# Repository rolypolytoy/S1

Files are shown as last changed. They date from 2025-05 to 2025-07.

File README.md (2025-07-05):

# S1 Desktop SEM

S1 is an open-source, low-cost, high-performance scanning electron microscope (SEM) project, which doubles as a reasonably accurate e-beam lithography machine, because why not?

| Metric            | Estimated     | Achieved | Method                  |
| ----------------- | ---------- | -------- | ----------------------- |
| Ultimate Resolution    |<<100nm     | TBD      | Reconstructing the Paper |
| Vacuum Pressure   | <10⁻⁵ Torr | TBD      | HV Diffusion Pump, Embedded Pressure Gauge.|

---

## System Overview

### Vacuum Integrity
View

[Roughing pumps](https://www.amazon.com/Orion-Motor-Tech-Conditioner-Servicing/dp/B08P1W6Z8D) can be bought quite cheaply on amazon for about $70, and can pump down to the 1e-2 torr order of magnitude, which is good enough as a backing pump for most high-vacuum pumps. This one is 37.5 microns, which converts to around 3e-2 torr, which is good enough for diffusion pumps.

Most pumps of this kind have an around 1/4th inch diameter outlet, and so you can buy 1/4th inch ID [vinyl tubing](https://www.amazon.com/Flexible-Lightweight-Plastic-Chemical-Resistant/dp/B09Y5R8SSL). 

Finally- FCStd files for the Diffusion Pump are uploaded [here](https://github.com/rolypolytoy/S1/blob/main/Vacuum%20Integrity) and at the [Diffusion Pump](https://github.com/rolypolytoy/diffusion_pump) project. It's already built to be integrated with 1/4th inch vinyl pipes, so simply slip the pipe around the machined diffusion pump. We also use KF25 flanges and conventional water cooling with a pump, to ensure it stays cold.

For the O-ring, buy 130 mm ID, 2 mm thickness [Nitrile O-rings](https://www.amazon.com/uxcell-Rings-Nitrile-125-2mm-Diameter/dp/B07HGCCHNZ) to seal the flange between the diffusion pump and the connector to the vacuum pump.

The holes on the side of the flanges are around 6.4 mm in diameter, so use 8 M6 to tighten, once the O-ring is inside the groove, and the connector has been welded to the frame. 

We'll use the [KJL 704](https://www.agarscientific.com/vacuum-diffusion-pump-fluids) diffusion pump oil for 125.77 pounds from agar scientific, which has an untrapped ultimate vacuum of 1e-7 to 1e-8 torr and trapped of 1e-11 torr. Kurt J Lesker also sells 500 ccs directly for [120 dollars](https://www.lesker.com/newweb/fluids/diffpumpoils-silicone-kjlc/), and so this is really good cost-price.

The nichrome wire I'm using can heat up to 800W so we're good in terms of heating since resistive heating implements are the only implements with 100% efficiency, and 800W is more than enough to heat a diffusion pump of this size and we're using a [server fan](https://www.amazon.in/Delta-Electronics-AFB1212GHE-CF00-120x120x-connector/dp/B004X2M2GG) with 241 CFM- it's noisy but it's better than a water cooling system I know that, so about 200W of dissipation might be viable.

We'll use dovetail sliding doors, nitrile tubing, and screw clamps for the sliding door.

### Embedded Systems

All power sources are kept outside and funneled in- this is because power supplies have electrolytic capacitors that will 100% burst in a vacuum. All our embedded stuff is designed to have none of this.

The power supply comes from mains through a plug, and we have a [10kVDC](https://ar.aliexpress.com/item/1005003518403820.html) power source, as well as a [60VDC](https://www.amazon.in/Adjustable-05-60Volt-Variable-Converter-600Watts/dp/B0F3KJ5VNP) power source that connects w/mains.

- **Microcontroller**:  
  - [Teensy 4.1](https://www.amazon.in/4-1-iMXRT1062-Development-soldered-Pre-soldered/dp/B0DP6M197Q) (no electrolytic capacitors, which make it safe for vacuum pressures due to no outgassing or capacitor ruptures)
  - Works with the Arduino framework with [Teensyduino](https://www.pjrc.com/teensy/td_download.html).

- **Electron Detector**:  
  - [Plastic scintillator with 425 nm emission](https://www.alibaba.com/product-detail/Polystyrene-Plastic-scintillator-material-equivalent-EJ_1601298622046.html?spm=a2700.7724857.0.0.6c196c9eovIgdM). It's a 10mmx10mmx1mm cuboid.
  - [Onsemi SiPM with 420 nm peak sensitivity](https://www.mouser.in/ProductDetail/onsemi/MICROFC-30035-SMT-TR?qs=byeeYqUIh0Mh9KJVNOFZEA%3D%3D). I've taken the CAD file for this and put it in the CAD folder. Its rise time is 0.6nS, and at 420nM it has over 40% of particles detected. It has a 300 ps pulse with a 600 ps pulse width. It has several white papers on its characteristics. In [this one](https://www.onsemi.com/pub/collateral/and9770-d.pdf) we can see its breakdown voltage is ~24.6 V and in [this one](https://www.onsemi.com/download/white-papers/pdf/tnd6262-d.pdf) we can see its recommended overvoltage is 5.0V so 30VDC is a very, very good voltage and we can make it with the 60V power supply with a basic voltage divider. They have either a fast pulse or a normal pulse mode, we'll use normal pulse mode. 
  - [Cremat CR-110](https://www.amazon.ae/CR-113-R2-1-Charge-Sensitive-preamplifier-Module/dp/B07BCQSBD8) charge-sensitive preamplifier (µs-long pulses, 7 ns rise time) to read current from the silicon photomultiplier, and it needs a +-10V (12V total) power supply. The pulses from this are 7ns in terms of rise time and decay slower. 
  - [Cremat CR-200-500ns](https://www.amazon.ae/Cremat-Inc-CR-200-500ns-R2-1-Shaping-Amplifier/dp/B07BD28Y7R?) pulse shaper (500 ns pulses) so the ADC can read from it. Needs the same power as the CR-110. Shapes it into Gaussian pulses and amplifies it a bit more post-CSA so this should be in the hundreds of mV/low V range, but regardless will be within the ADC's 16 bits of range.
  - The [AD7626BCPZ](https://www.mouser.in/ProductDetail/Analog-Devices/AD7626BCPZ-RL7?qs=%2FtpEQrCGXCwjx1S0Wpoj8A%3D%3D)- a 10 MSPS ADC (exceeds the 2 MSPS requirement for 500 ns pulses, with roughly 5 samples/pulse- good for SNR). So, we can quite easily sample at 2MHz with this signal processing pipeline which is good enough for electron microscopy. Uses LVDS so we'll definitely need a chip for it which is [this one](https://www.mouser.in/ProductDetail/Texas-Instruments/DS90CR286ATDGGRQ1?qs=8%2FmU9qzJpL9GnwtExKjdYg%3D%3D). So we have a functional design for an electron detection pipeline at fast enough speeds for our needs.

I'll obviously use a blue LED on the photomultiplier-cremat-ADC setup to see if it works before assembling the ET detector.

Some auxiliary setup information not in the CAD: 
The first two condenser lenses must have 920 turns and the objective lens 600 turns in a solenoidal arrangement inside the housing. 

The EE bit is done, all that remains is the embedded system code & companion app (Teensyduino and QT via PySide6, Pyintaller, PyUSB, PySERIAL on pypi respectively).

### CAD
I found an [old paper](https://github.com/rolypolytoy/S1/blob/main/SEM_Design.pdf) which outlines how to design a 10-nm resolution SEM with exact current, current densities (so of course we can reconstruct the gauge they used, which I did, and it's 14 AWG), condenser 1, 2, and objective lens specs, beam column design, full ray tracing with commercial FEM, and so the design work has been done already. Of course this means all the work we did in the electron column is useless but honestly basically guaranteeing nm-scale resolution is worthwhile. Even if we don't get 10 nm resolution, it's going to get sub-micron resolution. The condenser lens 1 is centered at 80mm below the Wehnelt cap aperture (at 100.45mm). The second condenser lens is centered at 165mm below, or at -64mm-ish. Final focus is at 301mm, and the assembly of the objective lens must end at 290mm. This is all, as per the latest CAD file, is entirely valid and so the dimensions are all entirely correct. 

Additionally I've finished the CAD for the electron column including the Wehnelt cylinder, anodes, and lenses. There wasn't information on the pole piece bore size in the SEM paper so I found a patent for a magnetic lens design and it showed that the normal range was from 1 mm to 3 mm, so I've taken a 4 mm bore diameter for the condenser lenses and 1 mm for the objective lens (US5563415A if you're looking for it, but I have the pdf in the repo regardless). It expired in 2015- [proof here](https://patents.google.com/patent/US5563415A/en?oq=5%2c563%2c415), so we're entirely able to use it. In general there are a lot of US patents on electromagnetic lenses [here](https://patents.google.com/?q=H01J37%2f141).

Another expired patent I found really useful is a full design of an SEM that expired in 1992: [US3924126A](https://patents.google.com/patent/US3924126A/en?q=H01J37%2f141). It's not as useful as the paper because it doesn't include full dimensions, but it's a sanity check and it has some useful information about alignment, some dimensions that weren't mentioned in the paper, and aperture-related info. So, another good source.

For the pole piece: one internal piece, one external piece, attached w/screws. 3A current, 2.8A current, 1.1 A current. 14 AWG wire. Center of condenser lens at 80mm, Focal position 1 at approx. 100mm, Center of Condenser 2 at 164mm, Focal position 2 at approximately 170 mm, center of Objective at 295mm and focal position at 315 mm. 1000 micrometer beam-limiting aperture at 80mm, 100 micrometer beam-limiting aperture at 200mm. Luckily all the apertures are 'inside' the lenses so we don't have to worry about them when constructing the structural parts.

A 500 micrometer aperture as the condenser aperture at 60 mm and a 200 micrometer aperture as the objective aperture at 280 mm.

We also need ~500m of 14 AWG aluminium wire which is either insulated or enameled, for as cheap as possible, which is roughly 14.5 USD, and definitely under 100

Every exterior of the EM lens should be in 4 pieces, and the pole piece as 1. Design the CAD files of these next. Scanning coils (solenoid), stigmators (octupole), and alignment coils (quadrupole) also necessary using 14AWG Al wire where relevant.

For the yoke of the magnetic lenses we'll use electrical steel, and for the pole piece we'll use 99.95% iron (electropolished and nickelplated ofc).

Make a singular CAD Assembly file with all details.

I've fully reconstructed the specs from the paper. Here's an exploded view of all the non-structural components- you can see the housing, pole pieces, Wehnelt caps etc etc:



Non-exploded view of the frame with diffusion pump attached:



View of all the analog & power electronics via a circuit schematic: 

Circuit

This is in the repo as Column.FCStd, of course. All the sizes are exactly as taken down to the mm from the paper, and I've made structural components for everything as well. The baseline weight of the frame is ~32 kg and if made of Al 6061 should cost on the order of $100, and the full frame w/sliding doors (metal to metal seal w/ambient air pressure pushing on it) is in Frame.FCStd.
      
  - **Cable feedthroughs**:
    -   Our current approach to making flanges is to, when the frame is being machined, make precise holes in the exterior, pass silicone wires through, and use vacuum-tolerant epoxy. This is expensive, but believe it or not, significantly less expensive than buying feedthroughs for 230VAC, 24VDC, USB, etc, etc. We use [Loctite Stycast-2850](https://in.rsdelivers.com/product/loctite/loctite-stycast-2850-ft-quartkit/loctite-loctite-stycast-2850-ft-quartkit-black-1/2349630)- a state of the art vacuum epoxy, which means this "makeshift" setup is actually more than satisfactory for HV, and really only gets iffy when you get down to UHV. Additionally- silicone doesn't outgas a lot, so using silicone-insulated wires isn't a no-no, but even if it is, taping over it with PTFE tape is an extremely easy (and cheap) workaround which doesn't compromise anything, or introduce any irregularities into the system.
  
  - **Stage platform**:
    - We use a cheap but micron-level accuracy open-loop stage by buying 3 instances of these [1-axis CNC stepper motor setups with 50 mm stroke length](https://ar.aliexpress.com/item/1005007308081154.html), combining it with three instances of the legendary [TM2209 motor driver](https://www.amazon.in/TESSERACT-TMC2209-V2-0-Ultra-Silent-Motherboard/dp/B08QPLL28G) which has 1/256 microstepping, which means we get micron-level resolution in XYZ. This is particularly important for beam clarity because this means we can use autofocus and vary the z-axis, instead of needing to vary the voltage to the objective lens, which makes our power electronics considerably simpler because we can just use static voltage dividers for all our high-voltage components and implement autofocus by modifying the z-axis and checking if the image is in-focus or out of focus. 

In-House Manufacturing for Al 6061 parts (via manual milling and lathes, for critical vacuum chamber bits sanding with 220 to 3000-grit), Polypropylene (via manual milling and lathing with up to 2000 grit), Soft Iron Yokes (via manual milling and lathing, surface finishing with 220 to 2000 grit), Pole Pieces from 99.95% iron (manual milling/lathing, then electropolishing then nickel plating). Before and after assembly clean everything with isopropyl then acetone, in a cleanroom-esque environment with nitrile gloves and basic PPE.

29/5/2025: I've begun looking for the 500 meters of 14/16 AWG Aluminium wire and the CAD components. Stuff's coming together. I'll keep updating this when there's more progress on this end. From what I can tell, getting electropolishing and nickel plating isn't going to be particularly challenging and since our tolerances are more surface finishes than actual manufacturing tolerances it's going to be easy enough to do 'in house'.

30/5/2025: Ordered every non-structural component, will see how things begin to come together. Ultimately, went easier than I expected. Thanks Agar Scientific, Mouser, Amazon, and AliExpress. Still need to find a supplier for 3N-4N soft iron and 500 meters of aluminum wire. I talked to a guy who sells the latter and he laughed me out for such a 'small quantity' asking me to get at least 50 kg (read: 10 km of wire) or not waste his time. You win some, you lose some. I'll provide updates as everything comes in.

31/5/2025: Teensy 4.1's already arrived, as have a few other miscellaneous things. It's fortuitous it arrived so quickly because it means I can troubleshoot my setup and understand the flow of this MCU well. I already have an Arduino kit, I'll solder headers onto it and in general prepare for the full setup prematurely.

12/6/2025: Several things have arrived. All the 3D printed parts are fabricated to within tolerances. The 10kV HV sources have also arrived, as have the ADC, DAC, SiPM, and Cremat signals processing modules. Still no electrical steel, but we've found a supplier for 500 meters of copper wire and ~200 meters have already arrived, with 300 more to go. Soft iron's also found (4N, from AliExpress once more). Progress is progressing.

19/6/2025: We're using soft iron ingots and melting and casting them, so the final supplier issue (on the materials side) is done, and we're officially to assembly. Like a hydra though, there's another issue- the Cremat CR-113 hasn't shipped and they've refunded it, and only the CR-200-500ns has shipped. So we're going to have to make a CSA with an op-amp in a differentiator setup in an SIP package. Doable with KiCAD, and it'll honestly be lower cost and higher perf, so I'm glad it happened. Maybe I'll remake the CSA + pulse shaper in one package, or make a full MCU + signals processing PCB instead of the whole Teensy, DAC, ADC, SiPM, signals processing as modules thing. For a prototype a difficult setup is fine but for production, definitely not. In more good news though- DRDO's [SSPL](https://www.drdo.gov.in/drdo/labs-and-establishments/solid-state-physics-laboratory-sspl), a SOTA government research laboratory in materials science, and Miranda House from Delhi University, are tentatively going to be beta-testers for it when the prototype is assembled, so there's already some steady footing in that direction.

5/7/2025: Bled over into early Q3 2025, which is unfortunate. But the frame is made! Onto machining the internals and assembling the embedded systems stuff. Looks really good so far. Fixed the Cremat CR-113 issue- made a bespoke CSA with 750x higher gain (better for low-current filaments) and half the cost of the 113. I call it [Lightning In A Bottle](https://github.com/rolypolytoy/lightning-in-a-bottle) because it's really good (the op-amp I used is the best on the market), cheaper than the CR-113 by >50%, and bottling charge is basically exactly what a charge integrator is. It's a better name than Cremat anyways. It's already ordered and should arrive in under 2 weeks from PCBPower, they've got all the parts on hand so no waiting around. I also learnt analog design as a side quest so it's probably good that Cremat refunded me.

---

## Development Timeline

| Milestone                            | Target Date |
|-------------------------------------|-------------|
| Full design complete   | ✅ Q1 2025   |
| **Release-ready version (BEHIND TARGET!!!! WE NEED TO GRIND!!!!!!!!)**           | 🟡 **Q2 2025** |
---

---
## Assembly Instructions

I'll update this with photos and instructions the further I get along in the process.

SEM frame:
SEM

3D printed parts:



- Machine it and get it functioning
- Get e-beam lithography tested and functional to <25 nm resolution.

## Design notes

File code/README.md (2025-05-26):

#Embedded/Electric

Power: 60V

TMC2209 (3 motors NEMA11) settings:
Driver 1: MS1=GND, MS2=GND (address 0b00)
Driver 2: MS1=VDD, MS2=GND (address 0b01)
Driver 3: MS1=GND, MS2=VDD (address 0b10)

50 mm stroke 1 mm pitch

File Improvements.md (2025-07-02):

Monolithic PCB for analog and digital processing- plugs in, plugs out etc.

Monolithic PCB for power electronics- main inputs, coax cable outputs for different powers.

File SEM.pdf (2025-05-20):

Journal of Mechanical Science and Technology 22 (2008) 1734~1746

www.springerlink.com/content/1738-494x DOI 10.1007/s12206-008-0317-9

Journal of

### Mechanical Science and Technology

## Design and fabrication of a scanning electron microscope using a finite element analysis for electron optical system

### Man-Jin Park¹

### , Dong Hwan Kim²

### , Keun Park²

,

### Dong Young Jang³

### and Dong-Chul Han⁴,*

1
School of Mechanical and Aerospace Engineering, Seoul National University, Shinlim-Dong San 56-1, Seoul 151-742, Korea 2 School of Mechanical Design and Automation Engineering, Seoul National University of Technology,
172 Gongreung-dong, Nowon-gu, Seoul 139-743, Korea 3
Department of Industrial Information and System Engineering, Seoul National University of Technology,
172 Gongreung-dong, Nowon-gu, Seoul 139-743, Korea 4
School of Mechanical and Aerospace Engineering, Seoul National University, Shinlim-Dong San 56-1, Seoul 151-742, Korea

(Manuscript Received December 28, 2007; Revised March 24, 2008; Accepted March 26, 2008)

--------------------------------------------------------------------------------------------------------------------------------------------------------------------------------------------------------------------------------------------------------Abstract

In this paper, we describe the design and fabrication of a thermionic scanning electron microscope (SEM) and examine its characteristics analytically. In the design process, the dimensions and capacity of the SEM components, such as the electron column, lenses, and apertures, were determined using finite element analysis. All components were integrated systematically during fabrication in order to achieve the maximum performance by adjusting the lens parameters, high voltage source, and image calibration methods. As a result, a thermionic SEM image with high resolution was achieved. We discuss the primary considerations required to achieve a high-performance image.

Keywords: Scanning electron microscope; Thermal emission; Electromagnetic lens; Finite element analysis --------------------------------------------------------------------------------------------------------------------------------------------------------------------------------------------------------------------------------------------------------

### 1. Introduction

With recent advances in nanotechnology, various
pieces of measurement and analysis equipment have become indispensable for measuring nanoscale objects. Successful research in nanotechnology depends on high-performance measurement or analysis equipment; therefore, the development of such equipment is of great importance. In particular, the scanning electron microscope (SEM) is an important tool used to observe surfaces and analyze nanoscale material components.
The history of electron microscopy began with the development of electron optics [1]. In 1926, Busch studied the trajectories of charged particles in axially symmetric electric and magnetic fields, and laid the foundation for geometrical electron optics when he showed that such fields could act as particle lenses. Nearly at the same time, the French physicist de Broglie introduced the concept of electron waves. A frequency and hence a wavelength was associated with charged particles: this marked the beginning of wave-electron optics. Following these two discoveries in electron optics, the idea of an electron microscope began to take shape [1].
SEMs can be classified into two groups: thermionic and field emission. A field emission SEM has the highest magnification capability and is widely used in industries and research [2-4]. However, field emission SEMs are extremely expensive and require a high level of precautions, including an ultra high vacuum and a clean room, compared to thermionic SEMs. The need for SEMs in the semiconductor industry continues to increase. However, the measurements are a slow process as the SEM scans the object using an

*
Corresponding author. Tel.: +82 2 880 7139, Fax.: +82 2 883 1513 E-mail address: dchan@amed.snu.ac.kr
© KSME & Springer 2008

M.-J. Park et al. / Journal of Mechanical Science and Technology 22 (2008) 1734~1746 | 1735

electron beam. To eliminate this drawback, a miniature and potentially portable SEM with small column dimensions or a multiple column arrangement has been developed [5, 6], but it suffers from poor resolution.
SEMs use extremely short wavelengths (smaller than the wavelength of visible light) to enhance the resolution. Compared to an optical microscope that uses a visible light source with a wavelength of 300 to 700 nm, SEMs use an electron source with a wavelength of 1 nm. The structure and principle of SEMs are similar to optical microscopes. Optical lenses for focusing light in optical microscopes are substituted by electromagnetic lenses for focusing electron beams in SEMs. The electromagnetic lenses cause the electron beam to focus or diverge, depending on the electric current applied on the coils.
In this article, we describe the design and fabrication of a thermionic compact SEM with better performance in terms of resolution and image stability. Our high-resolution SEM is user-controlled and operates using a monitor. Before designing our SEM, beam trajectory analyses in the SEM column were performed for various types of lenses and apertures using the OPERA-3D [7] software. These analyses provided guidelines that resulted in an efficient SEM. Optimal design aspects for various parameters, such as the number of apertures and their arrangement, the pole-piece design of the magnetic lenses, and the excitation current conditions for the magnetic lenses, were considered. We used the simulations to investigate the effect of these design parameters on the SEM performance.

### 2. System fabrication and experiments

A thermionic SEM consists of various mechanical and electrical parts, including an electron gun, a column, a stage, a chamber, electromagnetic lenses, and a controller generating an appropriate current in each coil. Fig. 1 shows a three-dimensional (3D) drawing of a thermal SEM. Fig. 2 illustrates all the components in the electron optical column of our developed SEM; each component was designed and placed to maximize the focusing capability and to enhance the resolution. It is evident from Fig. 2 that the SEM is not very large: the dimensions of the column and the chamber together are only 510 × 460 × 500 mm. The following sections describe the development of the key components of our thermionic SEM.

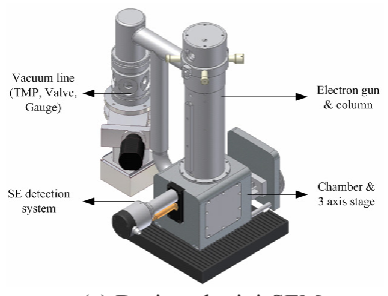
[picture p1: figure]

(a) Designed mini-SEM | (b) Case surrounding the mini-SEM

Fig. 1. 3D image of our fabricated thermal SEM:

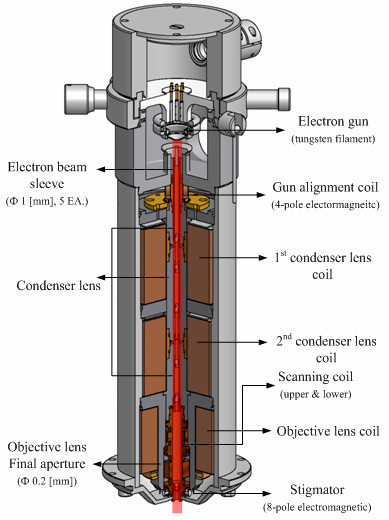
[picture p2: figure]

(a) Section view

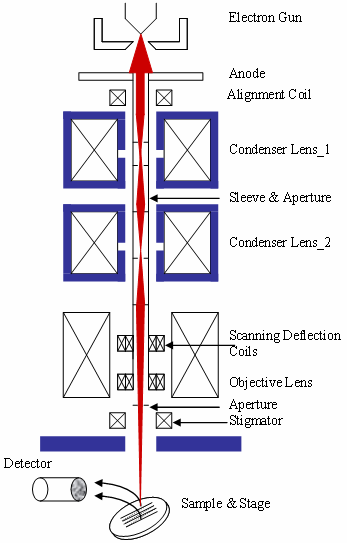
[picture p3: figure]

(b) Schematic diagram of the lens

Fig. 2. Assembled electron optical components (electron gun and electron optical column): (a) section view and (b) schematic diagram of the lenses.

1736 | M.-J. Park et al. / Journal of Mechanical Science and Technology 22 (2008) 1734~1746

### 2.1 Electron beam emission characteristics of ther-

mal electron gun

The electron gun consisted of three electrodes: the cathode, Wehnelt cylinder, and anode. The cathode consisted of a tungsten wire filament bent in the shape of a hairpin with a diameter of 0.15 mm. It decreased the electron beam diameter to guarantee minimal electron emissions at the filament end point. This filament operated stably at 2700 K. The cathode had a low work function (4.5 eV) and high mechanical strength to ensure long-term operation. Tungsten cathodes are widely used because they are both reliable and inexpensive. The Wehnelt cylinder induced the electron beam production from the cathode. It was fabricated and tested many times to ensure the reliability and stability of the electron beam source. The

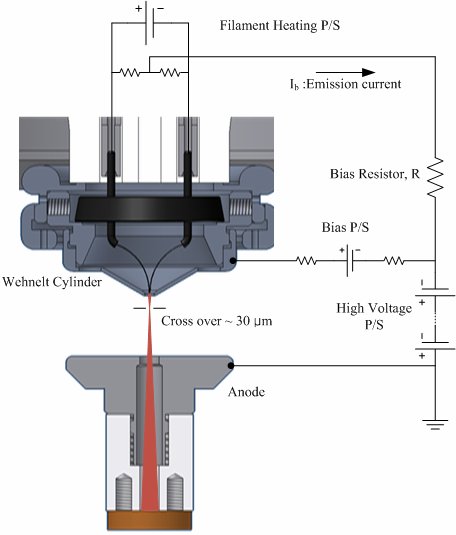
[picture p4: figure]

Fig. 3. Configuration of a thermionic emission gun.

anode was used to accelerate the electron beam after it left the cathode, induced by the Wehnelt cylinder. In addition to a high-voltage source, the electrical power system consisted of three parts that helped with the emission of electrons by controlling the heating of the filament, induction of the cathode, and acceleration of the electron beam. When scanning the electron beam, the high voltages applied on the electrodes should be stable without severe voltage ripples. Our fabricated high-power source had ripples that were less than 10⁻³ % of the reference voltage. The voltages applied on the tungsten filament, cathode, and Wehnelt cylinder ranged from -5 to 25 kV, and the anode was electrically grounded. The electrons emitted from the filament produced a crossover at the Wehnelt, which was under a negative biased voltage in the range of 3 kV, as shown in Fig. 3. The electrons were subjected to a strong acceleration towards the anode due to this high voltage difference between the cathode and the anode. The accelerated electrons reached the specimen through subsequent focusing lenses built in the electron optical column.
A half-fixed biased gun was employed to maintain a high stability and beam current in the gun structure. Thermal emission experiments were performed in a specially manufactured vacuum chamber; the vacuum level inside the chamber was maintained under 10⁻⁵ torr. The emitted electron beam went into a narrow sleeve that functioned as a wave guide and was made of a conductive phosphorous copper. The emitted electron beam current, which passed through a 5 mm hole, was measured at a Faraday cup connected to an electrometer (Keithley 6517) that could measure picoampere-level current. The electron beam was

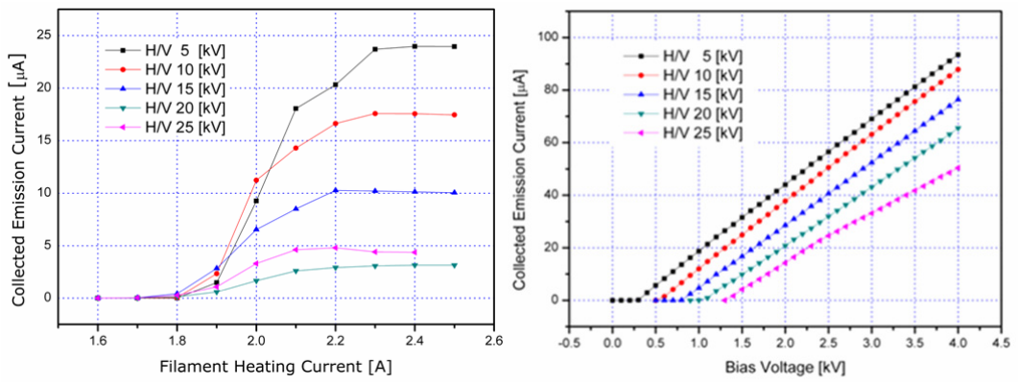
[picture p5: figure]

(a) Filament heating current | (b) Bias voltage

Fig. 4. Variation in the electron emission current with the filament heating current and bias voltage.

M.-J. Park et al. / Journal of Mechanical Science and Technology 22 (2008) 1734~1746 | 1737

aligned mechanically and electrically in the electron gun to measure the electron beam current at the Faraday cup. The beam emission currents were measured as shown in Fig. 4(a) by increasing the filament current from 1.6 through 2.6 A in steps of 0.1 A for five applied acceleration voltages (5, 10, 15, 20 and 25 kV). Around 2.3 A, the current reached a saturation point for all applied voltages. For each acceleration voltage, the changes in the emission current were also measured by changing the bias voltage; these results are illustrated in Fig. 4(b).
The emission current increased as a high bias voltage was imposed on the Wehnelt. Since the emission current and the bias voltage have a linear relationship, an appropriate bias voltage selection is recommended for a large electron beam.
The bias between the cathode and the Wehnelt is often produced by a simple feedback consisting of a resistor connected in series with the cathode. As the electron current emitted from the cathode increases, the cathode becomes more positive with respect to the Wehnelt so that the emitted current is stabilized. The preferred arrangement is to use an electric stabilizer circuit that monitors the beam current and alters the bias voltage to keep the current constant. The purpose of the Wehnelt electrode is to control the electric field close to the cathode so that electrons are emitted from only a small area of the cathode and are subsequently focused into a narrow beam suitable for further demagnification by a series of electron lenses to form the final electron probe. Normally such guns are designed and adjusted so that the electron beam is forced into a narrow “crossover spot” at a short distance beyond the anode, which is then demagnified to form the final probe.

### 2.2 Electromagnetic lenses

The lenses in a SEM play a vital role in demagnifying the electron beam to obtain a focused beam spot. A magnetic lens is most frequently used for narrowing the beam by driving a magnetic field-applied electric current on the coil[8]. By changing the coil current, the focal length can be adjusted, ensuring a highly focused beam. This magnetic flux causes the electron beam to deflect, which is explained by Lorenz’s law. We used two condenser lenses and one objective lens to demagnify the electron beam spot size down to a few nanometers from the large crossover diameter at the Wehnelt cylinder in the electron gun. The condenser lenses, objective lens, and lens apertures were installed serially along the beam trajectory axis, yielding a successively more focused electron beam. The condenser lens, located right after the anode, functioned as a first focusing device for the electron beam, while the second condenser lens also focused the electron beam to demagnify it again. The smaller the beam spot size achieved by the combination of the condenser lenses, the higher the resolution. Once past the condenser lenses, the electron beam was further focused by the objective lens before finally striking the specimen. The aperture was a small hole made of a non-magnetic refractory metal. It intercepted the electrons that passed through the periphery of the lenses and allowed only electrons in the dominant part of the whole electron beam to pass through. Several apertures were placed in the center of the electron beam. The size of the last aperture was predominant in determining the beam size, brightness, diverging angle, and depth of focus. The smaller the last aperture, the higher the resolution. This, however, results in a small number of electrons on the specimen. Therefore, a precise modulation of the aperture is necessary. In our SEM, six apertures were employed to enhance the resolution. The efficiency of the magnetic field was maximized to improve the performance of the electromagnetic lenses. Since the magnetic field depends on the coil current and number of turns, the lens parameters, such as beam energy, width of coils, and inner and outer diameters of the coils, lens geometry, and design, were determined with special care. A strong magnetic field can be obtained inside and outside the lens by focusing the distributed magnetic field. A soft and pure iron material was employed to generate a strong magnetic field

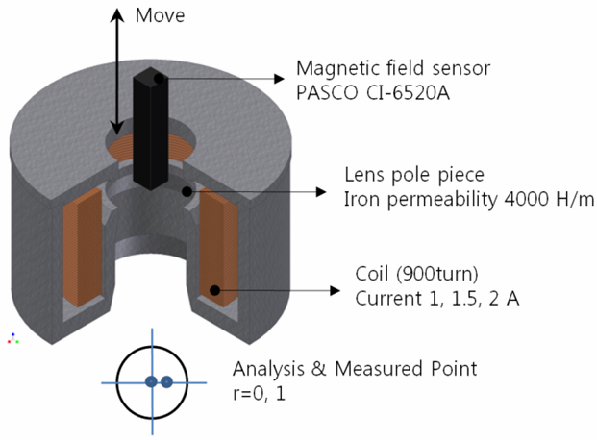
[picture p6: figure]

Fig. 5. Experimental system for measuring the magnetic field along the center of the lens.

1738 | M.-J. Park et al. / Journal of Mechanical Science and Technology 22 (2008) 1734~1746

in a specific area. The magnetic flux measurement
device is shown in Fig. 5 while the flux measurement
along the lens center is plotted in Fig. 6. Comparison
between numerical analysis and experimental results showed a good agreement, which indicates that the lens design was effective.
Our electron optical system consisted three magnetic lenses: two condenser lenses and an objective lens. These magnetic lenses played an important role in deflecting the electron beams so as to focus them at a specific point. In order to predict the beam trajectory, the electromagnetic field originating from the magnetic lenses was calculated using a finite element analysis [9].

### 2.3 Controller design

The controller in our SEM controlled all components and monitored the signals from the driver. We used a user-friendly fully digital controller rather than a classical analog one. The controlled SEM components included the high-voltage source of 2 to 25 kV, lenses to focus the electron beam, vacuum system to maintain the high vacuum inside the column and the chamber, scan generator to scan the electron beam

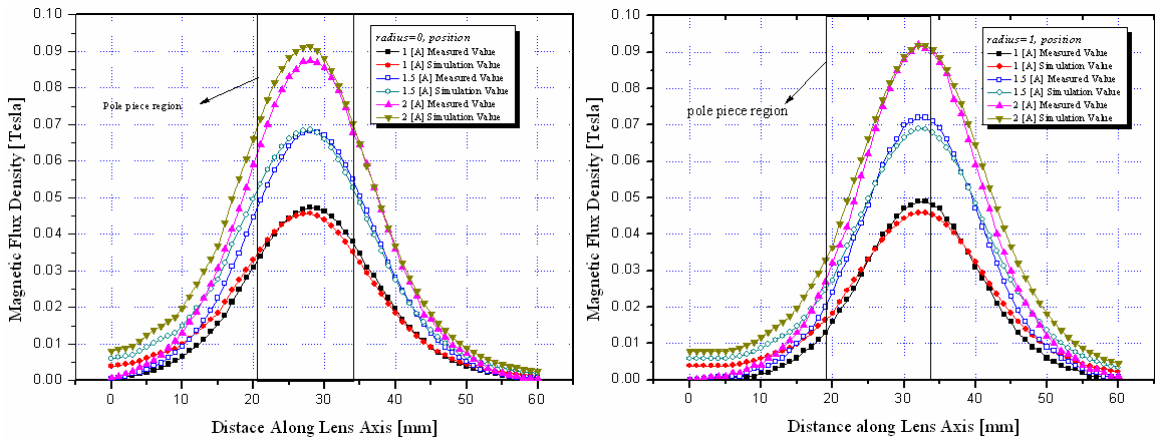
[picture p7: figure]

(a) Radius r = 0 | (b) Radius r = 1

Fig. 6. Comparison of the magnetic flux density obtained from experiment and numerical analysis.

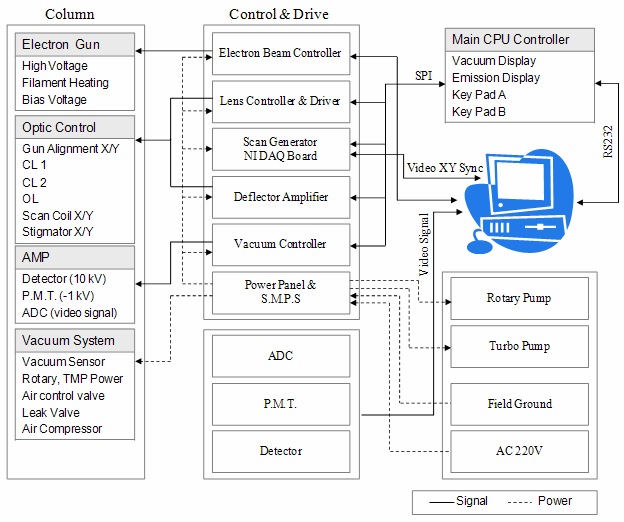
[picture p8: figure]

Fig. 7. Flow diagram of the SEM controller.

M.-J. Park et al. / Journal of Mechanical Science and Technology 22 (2008) 1734~1746 | 1739

along the specimen, amplifier to amplify the detected secondary electrons, and analog-to-digital (AD) converter to convert the amplified signal into a digital signal. The control flow for this system is shown in Fig. 7.
The electron beam control was located on top of the controller and used to control the electron gun. The lens currents that generated the magnetic field flowed into the coils to focus the electron beam. The values of the desired digitized currents were received from the main microcontroller, which was also connected to the main personal computer (PC) using a RS232 serial port. The scan generator that received synchronized video x and y-axis signals from the PC scanned the electron beam by sending signals to the lens controller and the deflection amplifier to set a certain magnification value. As the desired magnification value was obtained, the focused electron beam scanned the specimen, emitting numerous secondary electrons. Fig. 8 shows a diagram of the secondary electron detector. The emitted electrons were detected by a sensor located at the pre-amplification stage and were later amplified by a photo multiplier tube (PMT). This signal was digitally converted and fed into a universal serial bus (USB) data acquisition (DAQ) board (NI-6251, National Instruments) installed in the PC. The PC processed the acquired image signal and finally transmitted the image result to the monitor. The vacuum sensor and valve sensor checked the status of the chamber so that the vacuum value could also be displayed. The main digital signal processing (DSP) board controlled each controller, received the keypad input, and displayed the current value. The switching mode power supply (SMPS) supplied power to each controller while the power panel supplied electric power to the rotary pump, turbo pump, and leak valve.

### 3. Finite element analysis of the electron opti-

cal system

To design an efficient SEM system, we used finite element analysis⁹
to identify the optimal design criteria for focusing the beam under a magnetic field, encompassing the lenses, apertures, and electron beam source. The fabrication of our SEM was primarily based on this analysis, which suggested guidelines for the dimensions of each component and locations for those components inside the SEM. Precise measurements of the electron beam characteristics, such as spot size and density, cannot be easily obtained in a real SEM due to the limitations of the sensors installed inside it. Through this analysis, we demonstrated that the dimensions of the SEM components and their placement strongly affected the SEM resolution. Thus, a SEM design can be optimized using this numerical analysis. The finite element analysis indirectly demonstrated that the magnetic flux and electron beam deflection were dependent solely on the current on the coil.
Expensive equipment or special sensors to measure the physical quantities are not required when using simulated results. The theory and finite element analysis used to investigate the beam trajectory and focusing using various design parameters for the SEM components are described in the following sections.

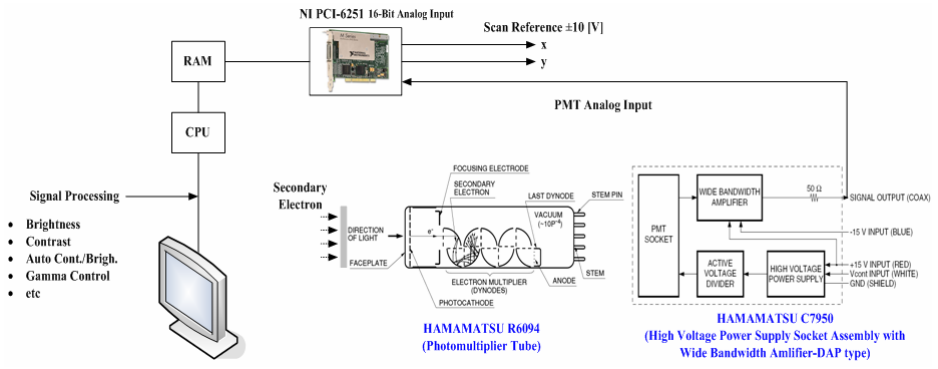
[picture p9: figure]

Fig. 8. Secondary electron collection and signal amplification.

1740 | M.-J. Park et al. / Journal of Mechanical Science and Technology 22 (2008) 1734~1746

### 3.1 Electron gun analysis

We simulated the gun structure as shown in Fig. 9.
The gun consisted of a hair-pin emitter, a Wehnelt
cylinder, an anode, a sleeve, and a Faraday cup. Electrons were accelerated to about -15 kV by the anode potential. In the simulation, the Wehnelt cylinder voltage was set to -15 kV [-70 to +40 V], the Wehnelt cylinder hole diameter was 1.5 mm, the distance between the emitter and Wehnelt cylinder was 1 mm, and the distance between the Wehnelt cylinder and the anode was 5 mm. Along the route from the emitter to the anode, the paths of the individual electrons crossover. The real source in an electron gun is projected onto the specimen surface to generate an image. The condenser and objective lenses then produce a demagnified image of the crossover on the specimen

by subsequent focusing.
The electron beam emitted from the filament forms a crossover at a specific point as a function of the negative bias voltage applied on the Wehnelt cylinder. Therefore, a simulation was performed to determine the emission characteristics, including spot size and emission current, as a function of the bias voltage. The results are illustrated in Fig. 10(a) and (b). In both cases, the bias voltage was changed from -70 V to 40 V at an increment of 10 V. The spot size increased linearly with the value of the bias voltage, as shown in Fig. 10(a). However, the emission current detected at the collector decreased with increasing bias voltage. This indicates that the emitted electrons formed the crossover as a function of the applied bias voltage, which can be used to control the dispersion

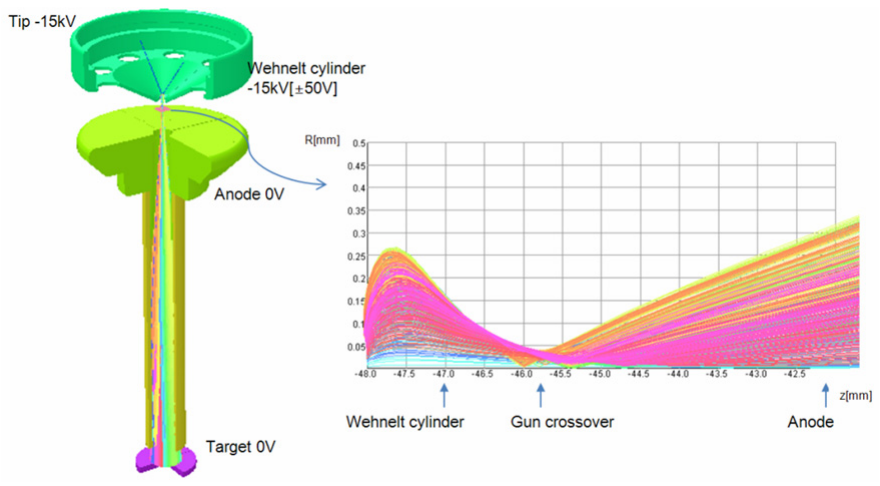
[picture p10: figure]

Fig. 9. Gun structure and simulated electron beam trajectories.

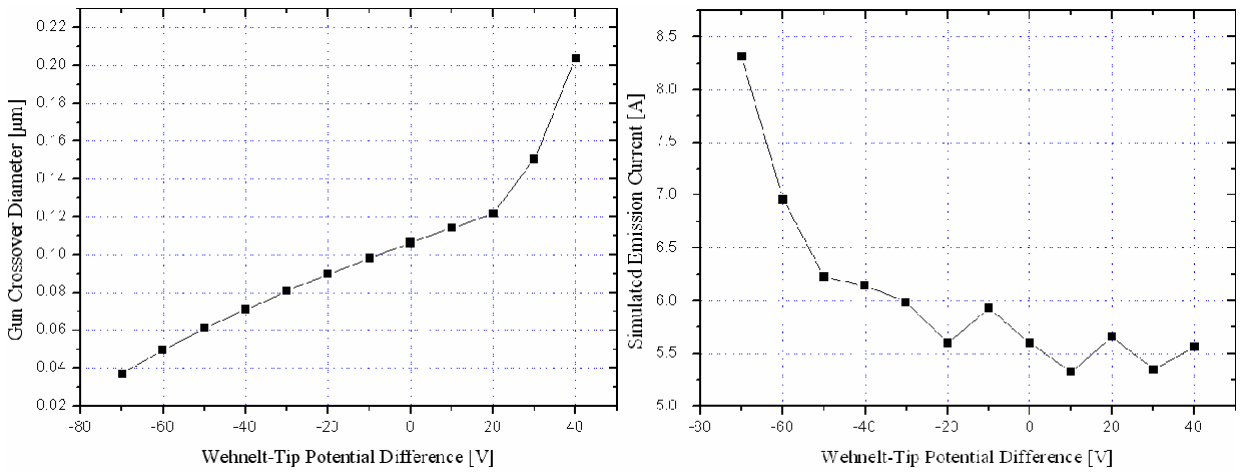
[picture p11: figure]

(a) Crossover diameter | (b) Emission current

Fig. 10. (a) Crossover diameter and (b) emission current as a function of the negative bias voltage applied on the Wehnelt cylinder.

M.-J. Park et al. / Journal of Mechanical Science and Technology 22 (2008) 1734~1746 | 1741

angle. The minimum crossover and the highest emission current were 36 µm and 8.3 µA, respectively, at a bias voltage of -70 V.
The variation in the beam spot radius as a function of the axial distance is shown in Fig. 11. The bias voltage was set to -70 V. The minimum spot radius at the crossover position, approximately 2.3 mm from the Wehnelt, was 0.06 mm.
If the round tip of the electron gun is rotationally symmetric, it can provide a good test of the significance of the details in the emission modeling. The spot size and crossover position on the optical system are critical for this application.

### 3.2 Electro-magnetic field analysis of the lens system

The electromagnetic lens characteristics were also analyzed by a finite element analysis. The validity of this approach was demonstrated by experiments. In general, the pole piece gap in the magnetic lens is designed to be as small as possible to increase the magnetic flux intensity. This, however, makes it difficult to measure the magnetic flux. An experimental lens was designed and fabricated to resolve this issue. A schematic diagram for the lens is depicted in Fig. 5. Considering the axisymmetric properties of the lens, an electromagnetic analysis was performed using OPERA 3D based on a 3D axisymmetric shape. The magnetic flux generated from the coil easily penetrated the relatively high-permeable pure iron and was concentrated near the pole piece. To measure the effect quantitatively, the magnetic fluxes Bz and Br

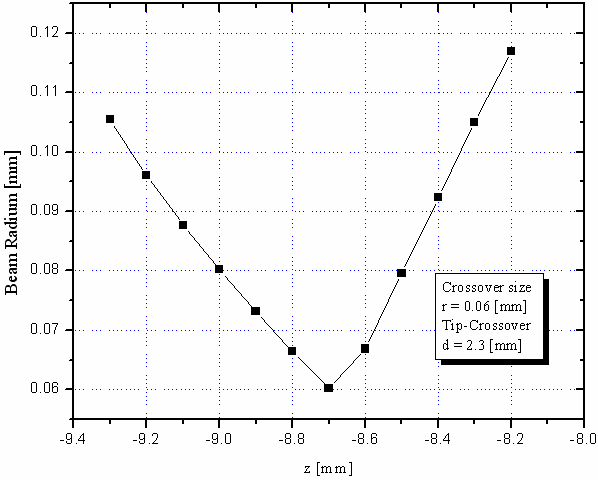
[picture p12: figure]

Fig. 11. Variation in the beam spot radius as a function of the axial distance.

were measured as a function of distance from the lens center.
From the (B-H) curve of pure iron, the permeability of the linear region of the curve was estimated as 4000 [H/m]. To compute the focal length of the condenser lens, the magnetic flux must be measured (or estimated by numerical analysis) exactly. The magnetic flux distributions near the pole piece were obtained from OPERA 3D/TOSCA, and the results are shown in Fig. 12.
Table 1 summarizes basic specifications of the coils and the corresponding current densities for the three magnetic lenses. The lenses were designed using axisymmetrical magnetic lenses with a gap width of 2 mm and diameter of 5 mm, and an unsymmetrical objective pole piece.
Fig. 12 shows the magnetic flux distributions around the two condenser lenses and the objective lens. Fig. 13 shows the magnetic flux distribution in the electron optical system. The magnetic flux for each lens is plotted as a vector plot under a given current condition. Most of the magnetic fields were distributed at the region of the pole piece. If the magnetic flux density did not exceed 2.0 Tesla, the column material could be magnetized. Except for the region around the lens, however, the magnetic flux of the housing material represented less than 1 Tesla. The direction of the applied current was the same as that of the magnetic flux. Thus, the magnitude of the magnetic flux around the pole piece acting as a lens represented the maximum value. On the contrary, the magnetic flux in the radial direction represented the minimum value. Based on this fact, the focal length of the electron beam had changed.
Therefore, lens characteristics can be driven by controlling both the coil current and the shape of the pole piece, and it is possible to determine the relationship between the applied current and pole piece shape.

Table 1. Basic specifications of coils for the three magnetic lenses.

Lens Type

No.
of
turns

Outer
diameter
(mm)

Inner
diameter
(mm)

Height
(mm)

Current
density
(A/mm²
)
Condenser
lens (1) | 920 | 78 | 26 | 65 | 1.36 - 1.88

Condenser
lens (2) | 920 | 78 | 26 | 65 | 1.25 - 1.74
Objective lens | 600 | 84 | 46 | 55 | 0.40 - 0.68

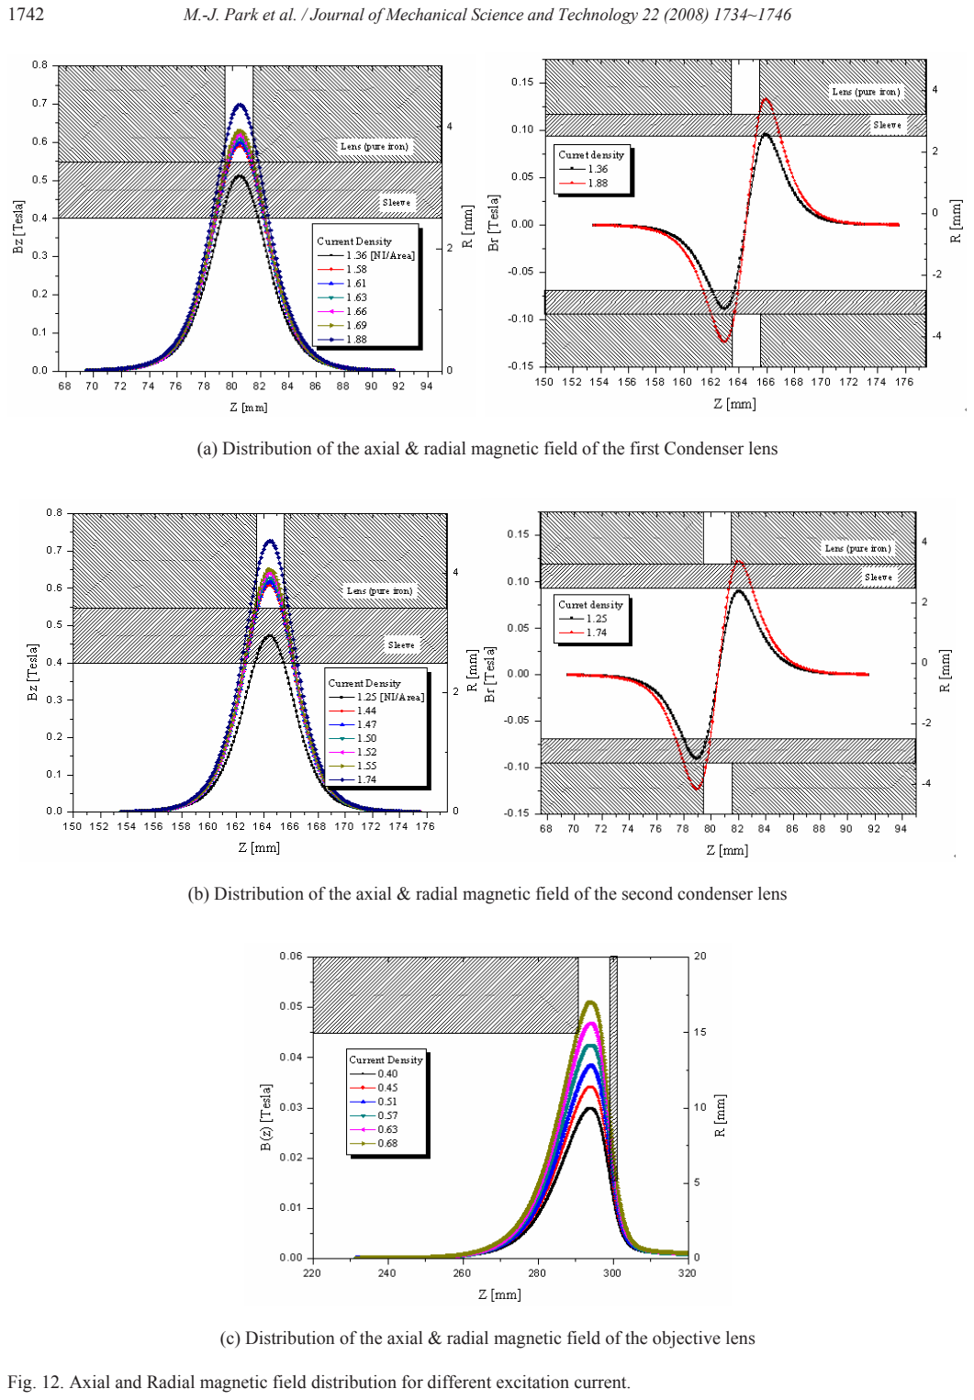
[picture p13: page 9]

1742 | M.-J. Park et al. / Journal of Mechanical Science and Technology 22 (2008) 1734~1746
(a) Distribution of the axial & radial magnetic field of the first Condenser lens
(b) Distribution of the axial & radial magnetic field of the second condenser lens
(c) Distribution of the axial & radial magnetic field of the objective lens

Fig. 12. Axial and Radial magnetic field distribution for different excitation current.

M.-J. Park et al. / Journal of Mechanical Science and Technology 22 (2008) 1734~1746 | 1743

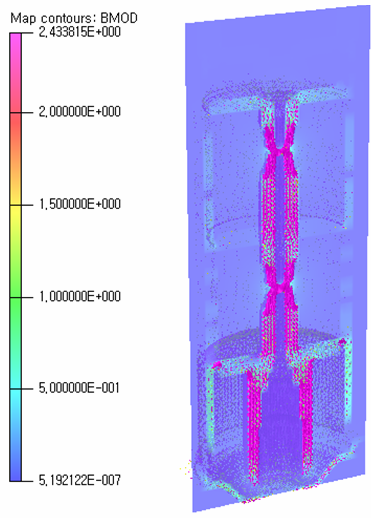
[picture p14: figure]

Fig. 13. Distribution of the magnetic potential in the electron optical column.

### 3.3 Space charge analysis for the electron optical

system

OPERA-3D/SCALA was used for the space charge analysis. The first and second condenser lenses and objective lens were added to the analysis model to consider the effect of the magnetic lens, as shown in Fig. 14. The axial length of the analysis domain was set to 320 mm. A finite element mesh was constructed for a quarter section of the model considering the geometric symmetry. An acceleration voltage of 15 kV was applied to the tungsten filament, and a bias voltage of -70 V was applied to the Wehnelt. Fig. 15(a) shows the resulting beam trajectory through the entire column. Fig. 15(b) and (c) show enlarged views of the trajectory around the gun region and the objective lens, respectively. The discharged electron beams were deflected due to the magnetic fields and converged to a specific region having a certain spot radius. Three lenses were modeled to investigate the magnetic flux, which determines the electron beam trajectory. The electron beams were discharged on the tip of the filament (z=-11 mm), and proceeded through the anode and sleeve. Beams that passed into the sleeve hole were refracted due to the magnetic field originating from the condenser lens, and focused to a point at an axial distance of 99.5 mm. The beams then diverged after the first crossover, and converged again due to the magnetic field of the second lens.

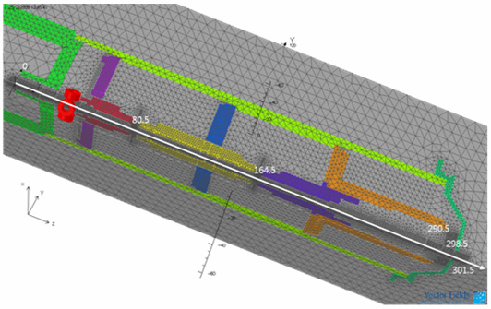
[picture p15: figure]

Fig. 14. 3D Model of the SEM column (gun, condenser and objective lens).

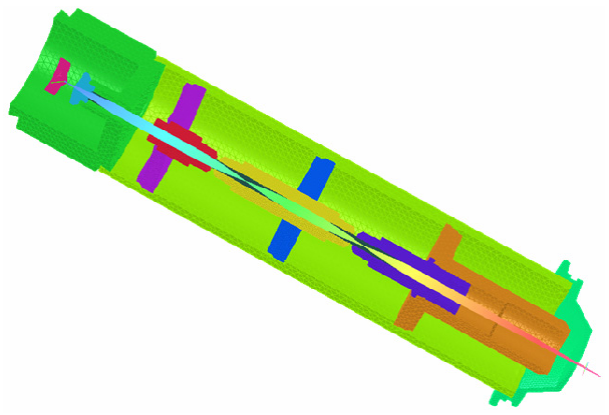
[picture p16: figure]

(a) Beam trajectory through the entire column

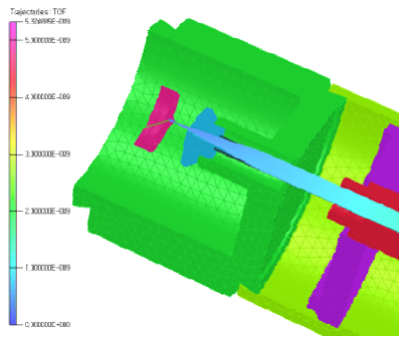
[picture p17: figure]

(b) Enlarged view in the gun region

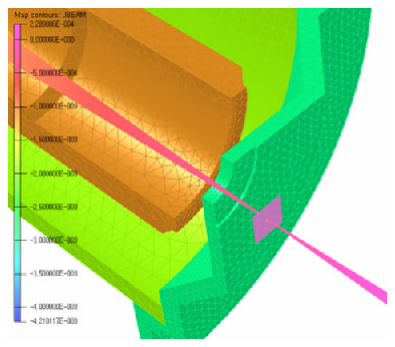
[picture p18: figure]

(c) Enlarged view around the objective lens

Fig. 15. Beam trajectory results inside the designed SEM column.

1744 | M.-J. Park et al. / Journal of Mechanical Science and Technology 22 (2008) 1734~1746

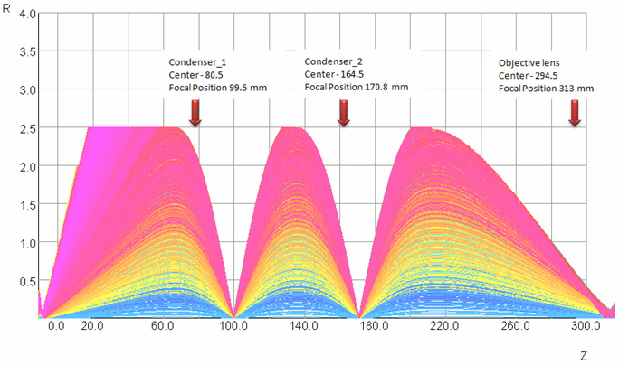
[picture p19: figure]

(a) Without apertures

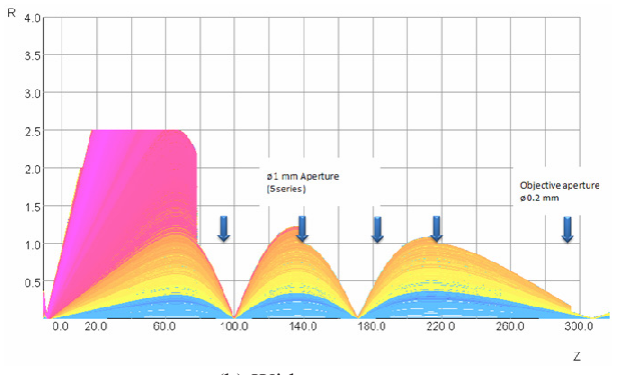
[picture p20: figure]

(b) With apertures

Fig. 16. Ray tracing results from the beam source to the image plane (a) without apertures (b) with apertures.

Fig. 16 shows the beam trajectory estimated by solving the ray-tracing equation. Two situations were considered: (a) one without apertures, and (b) one with apertures. The crossover size could be reduced by employing a set of apertures. The emitted beams were refracted and crossed twice due to the magnetic field generated by the two condenser lenses. The first and the second crossing positions corresponded to axial distances of 99.5 and 170.8 mm from the beam source, respectively. The crossover size was small and the aberrations were decreased if apertures were installed between the lenses.
Several aspects must be taken into consideration when designing a high-performance SEM. First, if the distance between two condenser lenses is kept to a minimum, it prevents the electron beam from going out of the center of the lens as long as a sufficient beam current is generated. If the distance is excessively large, then the beam hits an undesirable location, thereby reducing the electron density. Second, to minimize aberration, each aperture diameter must be adjusted to be in the range of 1 mm. Five apertures should be employed to maintain a high resolution. To further improve the resolution, we placed multiple apertures with different sizes inside the long sleeve.

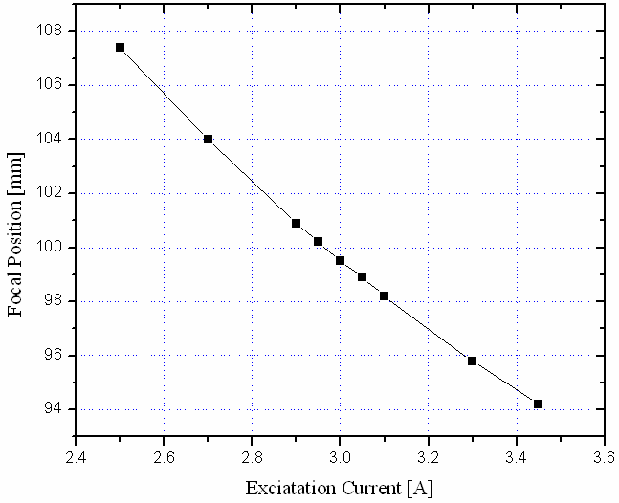
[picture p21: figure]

(a) Condenser lens 1

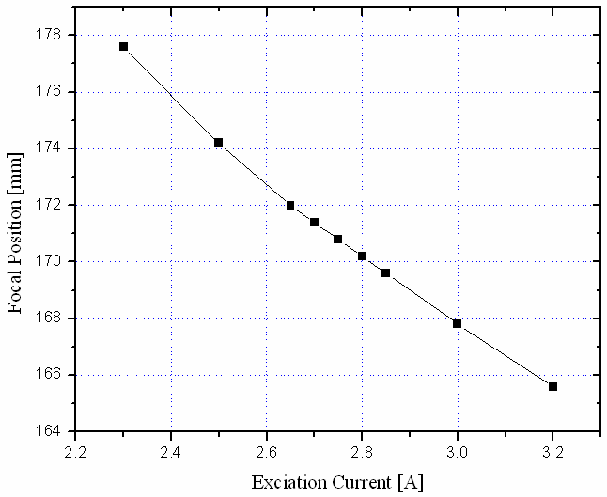
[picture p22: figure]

(b) Condenser lens 2

Fig. 17. Focal position for condenser lens 1 (a) and 2 (b).

The inner surface of the sleeve was machined well to have a low surface roughness, minimizing the external interference on the beam trajectory and reinforcing the magnetic field intensity.
An objective lens focuses the beam on the specimen, but it cannot produce an infinitely small spot size due to lens aberrations. Instead it produces a narrow spot that represents a demagnified image of the beam source. The diameter of the spot can be controlled, for example, by reducing the focal length of the objective lens, which results in a spot with a smaller diameter on the specimen. In general, the smaller the spot size, the better the resolution. It becomes increasingly difficult to resolve any two structures whose spacing is less than the diameter of the beam of charged particles. Thus, the spot size is crucial for image quality.

M.-J. Park et al. / Journal of Mechanical Science and Technology 22 (2008) 1734~1746 | 1745

The focal position is proportional to the current supplied to the lens windings. Changing this current density allows the focusing power of the lens to be varied (see Fig. 17). The focal position can be sufficiently varied, meaning that an electron image can be focused by adjusting the lens current.

### 4. Performance specifications

The performance of the fabricated SEM was verified by observing the specimen images. Test samples of 25- and 100-µm nickel mesh were placed on the specimen holder located in the chamber. Scanned images of the sample are shown in Fig. 18. The ball shaped object could be clearly identified, and the edges of other adjacent objects were also distinctly visible by increasing the magnification and adjusting the focus of the condenser and object lenses.

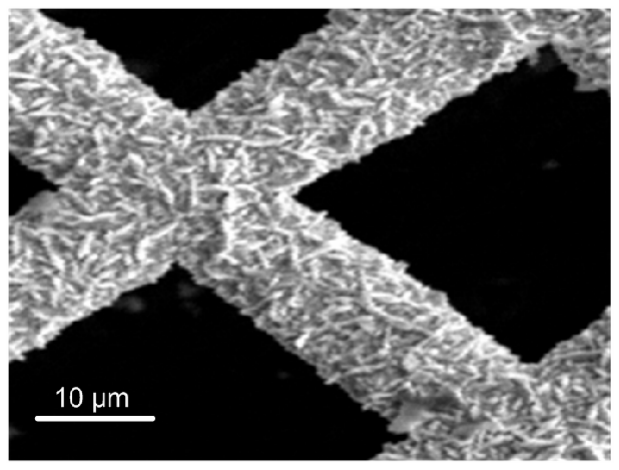
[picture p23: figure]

(a) 25 µm nickel mesh

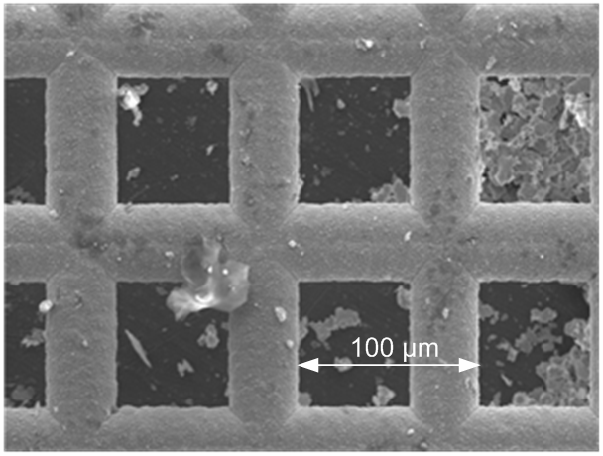
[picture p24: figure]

(b) 100 µm mesh sample

Fig. 18. SEM images for a 25 µm nickel mesh sample (a) and 100 µm mesh sample (b).

A high resolution of about 10 nm was achieved. This was estimated from the 6,000× SEM image (image on the left of Fig. 18) at an accelerating voltage of 15 kV. Guided by the simulation results, the dimensions and location of the lenses, apertures, and beam source, and the accelerating voltage were optimally determined for the SEM design and fabrication. These parameters resulted in reduced chromatic aberration, improved beam brightness, even at low-electron probe energies, and reduced beam energy dispersion. When the dimensions or locations of the SEM components were changed, the simulation was able to predict or estimate the beam characteristics very accurately. The detector was able to reliably obtain the amplified signal of the emitted secondary electrons from the specimen. If the acceleration voltage was always stabilized with negligible level of ripples, the SEM image was stable and robust. For our setup, the high-voltage source was fabricated to meet our voltage variation criterion of less than 10⁻³ % ripples, resulting in stable and reliable SEM images. The applied currents on the electromagnetic lenses were about 80 mA; this current was precisely controlled by a 12-bit A/D converter from the digital controller. The applied current to each coil could be more precisely adjusted using our digital controller rather than a conventional analog controller, contributing to a higher-resolution SEM image.

### 5. Conclusion

A compact thermionic SEM was designed and fabricated, and its performance was tested repeatedly to demonstrate its high performance and stability. After several trials, a high resolution was obtained. The SEM images were stable, which implies that the beam focusing components were fabricated satisfactorily and located appropriately inside the column and chamber. In the design process, the placement and dimensions of the electromagnetic components were analyzed and identified by a finite element simulation using commercial electron beam analysis software (OPERA-3D/SCALA, TOSCA). Computer simulations were successfully used as a design tool to optimize the electron beam motion. The mechanical and electrical parts were optimized through several iterations of experiments and through simulation. Direct and precise measurements of the electron beam trajectory after it passes through the condenser lenses or

1746 | M.-J. Park et al. / Journal of Mechanical Science and Technology 22 (2008) 1734~1746

object lens are almost impossible, and the dimensions
of the lenses and apertures and their location in the
column cannot be determined easily. These challenges could be overcome by utilizing finite element analysis. After a SEM is fabricated, strict calibrations of each component are inevitably required to obtain a high-resolution image with extremely small aberrations. We expect that a more precise adjustment of our lenses and apertures, and their optimal placement could further increase the resolution.
We claim that despite being smaller, the performance of our fabricated SEM is on par with other commercial SEMs.

Acknowledgement

The authors would like to thank the support for from the Seoul R&BD program under Grant No. 10583, the Institute of Advanced Machinery and Design at Seoul National University and Grant No. 10011365, funded by the Ministry of Commerce, Industry and Energy.

References

[1] A. Bogner, P.-H. Jouneau, G. Thollet, D. Basset, and C. Gauthier, A history of scanning electron microscopy: Towards wet-STEM imaging, Micron, 38 (2007) 390-401.
[2] W. K. Lo, G. Parthasarathy, C. W. Lo, D. M. Tanenbaum, H. G. Craighead and M. S. Isaacson, Titanium nitride coated tungsten cold field emission source, Journal of Vacuum Science and Technology B, 14 (6) (1996) 3787-3791.
[3] A. V. Crewe, D. N. Eggenberger, J. Wall and L. M. Welter, Electron gun using field emission source, Review of Scientific Instruments, 39 (4) (1968) 576-583.
[4] H. W. Mook and P. Kruit, Optics and design of the fringe field monochromator for a Schottky field emission gun, Nuclear Instruments and Methods in Physics Research A, 427 (1999) 109-120.
[5] R. Y. Lutsch and E. Plies, Initial resolution measurements of miniaturized electrostatic lenses for LVSEM, Ultramicroscopy, 93 (2002) 339-345.
[6] H. S. Kim, D. W. Kim, S. Ahn, Y. C. Kim, J. Cho,
S. K. Choi and D. Y. Kim, Arrayed microcolumn operation with a wafer-scale Einzel lens, Microelectronic Engineering, 78-79 (2005) 55-61.
[7] Vector Fields Ltd., OPERA-3D/TOSCA: Reference Manual, 2004.
[8] P. W. Hawkes, Magnetic Electron Lenses, Springer-Verlag, Berlin, 1982.
[9] K. Park, H. Jung, M. J. Park, D. H. Kim and D. Y. Jang, A study on design and analysis for magnetic lenses of a scanning electron microscope using finite element method, Journal of the Korean Society for Precision Engineering, 24 (9) (2007) 95-102.

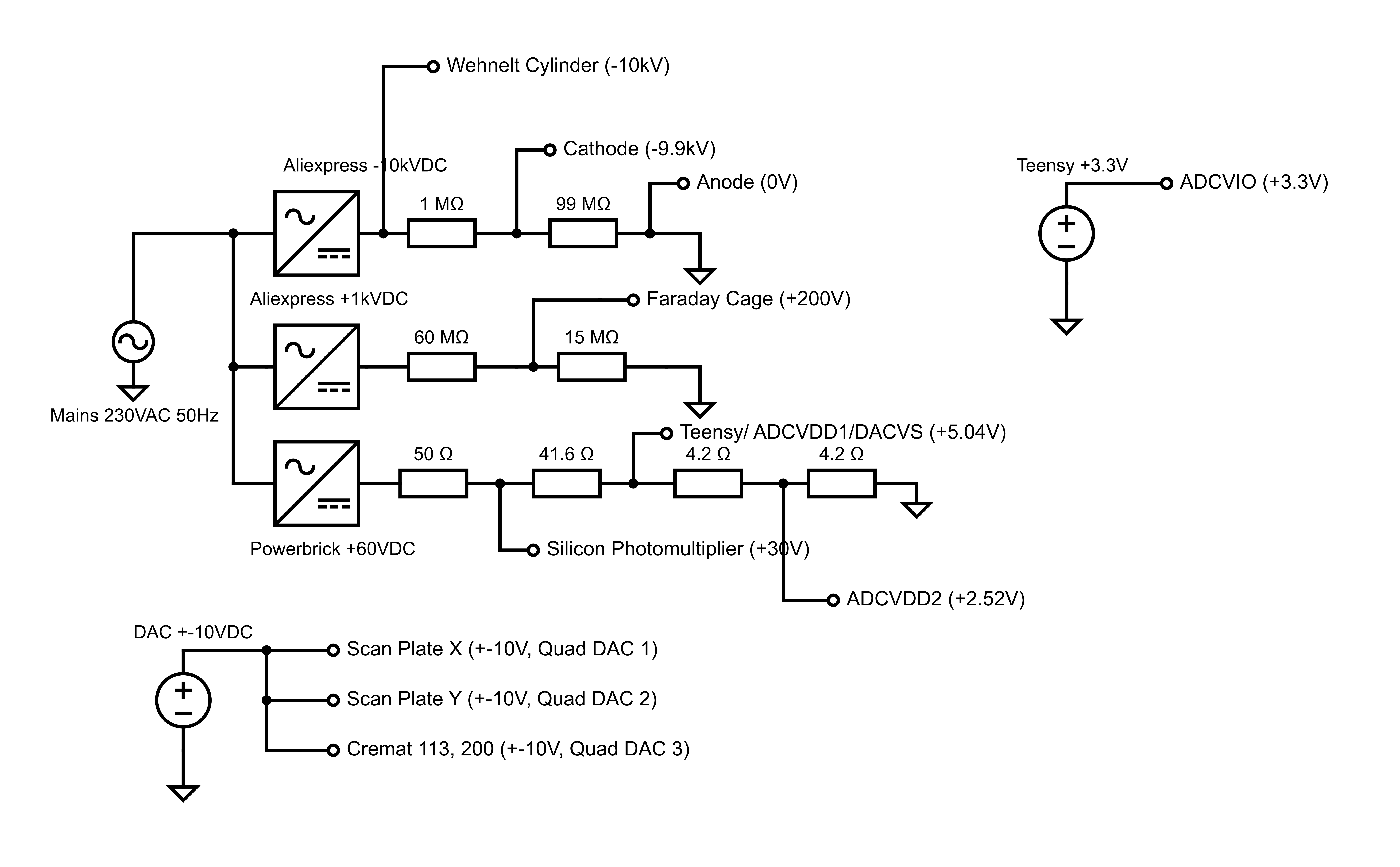
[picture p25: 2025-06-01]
code/Circuit.png

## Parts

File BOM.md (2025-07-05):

# Bill of Materials - Electron Microscope

## Electron Column

| Component | Description | Link | Cost (INR) |
|-----------|-------------|------|------------|
| Electron Gun | AEI AGA054 Tungsten Thermionic Filament (Package of 10) | [Agar Scientific](https://www.agarscientific.com/agar-filaments) | 10,560 |
| High Voltage Power Supply | 2x 230VAC 50W 10kVDC 5mA Power Supply (CX-50) | [AliExpress](https://ar.aliexpress.com/item/1005003518403820.html) | 1,200 |
| Low Voltage Power Supply | 60V 10A Adjustable Variable Converter 600W | [Amazon India](https://www.amazon.in/Adjustable-05-60Volt-Variable-Converter-600Watts/dp/B0F3KJ5VNP) | 4,999 |
| Linear Stages | 3x Linear (XYZ) Stage with NEMA-11 Stepper Motors (50mm stroke, 1mm pitch) | [AliExpress](https://ar.aliexpress.com/item/1005007308081154.html) | 4,000 |
| Beam Limiting Aperture | Platinum-Iridium 2mm OD, 100μm ID (Part No. 60100) | [Agar Scientific](https://www.agarscientific.com/tem/apertures/apertures-2-0-x-0-6mm-platinum-iridium) | 6,481 |

**Electron Column Subtotal: ₹27,240**

---

## Vacuum System

| Component | Description | Link | Cost (INR) |
|-----------|-------------|------|------------|
| Vacuum Gauge | HX710B Pressure Sensor Module (0-40KPA) | [Amazon India](https://www.amazon.in/HX710B-PRESSURE-0-40KPA-SENSOR-MODULE/dp/B0B662SYNH) | 290 |
| Diffusion Pump Heater | Nichrome Wire 330x4.0mm for Resistance Heating | [Amazon India](https://www.amazon.in/Filfora-Nichrome-Resistance-Heating-330x4-0mm/dp/B0CVTR7J1D) | 450 |
| O-Rings | 130mm x 3.5mm Nitrile O-Ring (Pack of 12) | [Amazon India](https://www.amazon.in/Oring-130-3-5mm-Pack-12pc/dp/B08PTCKJ3Y) | 599 |
| Cooling Fan | Delta Electronics 240 CFM Server Fan (120x120x38mm) | [Amazon India](https://www.amazon.in/Delta-Electronics-AFB1212GHE-CF00-120x120x-connector/dp/B004X2M2GG) | 9,390 |
| Silicone Oil | KJLC 704 Vacuum Diffusion Pump Fluid | [Agar Scientific](https://www.agarscientific.com/vacuum-diffusion-pump-fluids) | 13,000 |
| Viton Strips | Viton Rubber Strip (1m Length, 2mm Thickness) | [Amazon India](https://www.amazon.in/Rubber-Strip-Length-Thickness-Backing/dp/B0BL5PBXGG) | 2,900 |
| KF Flanges | KF-25 Aluminum Quick Clamp Vacuum Fittings Set | [Ubuy India](https://www.ubuy.co.in/product/6L1JO7TS-kf-25-aluminum-quick-clamp-kf25-flage-size-nw-25-quick-flange-clamp-with-wing-nut-closure-centering-)

**Vacuum System Subtotal: ₹26,629**

---

## Embedded Systems

| Component | Description | Link | Cost (INR) |
|-----------|-------------|------|------------|
| Microcontroller | Teensy 4.1 iMXRT1062 Development Board (Pre-soldered) | [Amazon India](https://www.amazon.in/4-1-iMXRT1062-Development-soldered-Pre-soldered/dp/B0DP6M197Q) | 3,900 |
| USB Cable | USB to MicroUSB Braided Charging Cable | [Amazon India](https://www.amazon.in/amazon-basics-Braided-Charging-Transfer/dp/B0CH1499X7) | 129 |
| Relay Module | 8-Channel Optocoupler Relay Module | [Amazon India](https://www.amazon.in/CLUB-BOLLYWOOD-Channel-Optocoupler-Insulation/dp/B0C2PT1KRB) | 617 |
| DAC | AD5754BREZ 16-bit 4-Channel Digital to Analog Converter | [Mouser India](https://www.mouser.in/ProductDetail/Analog-Devices/AD5754BREZ?qs=NmRFExCfTkE9WVZYrblgWQ%3D%3D) | 2,700 |
| ADC | AD7626BCPZ-RL7 16-bit Single Channel ADC (10 MSPS) | [Mouser India](https://www.mouser.in/ProductDetail/Analog-Devices/AD7626BCPZ-RL7?qs=%2FtpEQrCGXCwjx1S0Wpoj8A%3D%3D) | 6,500 |
| Epoxy Resin | J-B Weld Original Cold-Weld Steel Reinforced Epoxy | [Amazon India](https://www.amazon.in/J-B-Weld-Original-Cold-Weld-Reinforced/dp/B0006O1ICE) | 759 |
| Resistor Kit | Carbon Film Resistor Assortment Kit (1% Tolerance) | [Amazon India](https://www.amazon.in/Kinds-Value-Resistor-Assortment-electronic/dp/B08WKJPY5M) | 245 |

**Embedded Systems Subtotal: ₹14,850**

---

## Everhart-Thornley Detector

| Component | Description | Link | Cost (INR) |
|-----------|-------------|------|------------|
| Copper Mesh | Copper Mesh for Faraday Cage/EMI Blocking | [Amazon India](https://www.amazon.in/Copper-Mesh-Prefect-Blocking-Eco-Friendly/dp/B08PSLHWZT/) | 2,300 |
| Scintillator | Polystyrene Plastic Scintillator Material (EJ200 Equivalent) | [Alibaba](https://www.alibaba.com/product-detail/Polystyrene-Plastic-scintillator-material-equivalent-EJ_1601298622046.html) | 3,100 |
| Optical Coupling | 99.7% Vegetable Glycerin (Optical Coupling Gel) | [Amazon India](https://www.amazon.in/Chemtex-Glycerine-Vegetable-Emulsifier-Sweetener/dp/B09KRYXW67) | 650 |
| Lightguide | PMMA Acrylic Block (Versatile Rectangular) | [Amazon India](https://www.amazon.in/UraXx-Versatile-Rectangular-Limitless-Possibilities/dp/B0CGNCHX6W) | 200 |
| Optical Cladding | Aluminium Foil (72 Micron) | [Amazon India](https://www.amazon.in/Ezee-Aluminium-Foil-72-Micron/dp/B00Y0Q073A) | 450 |
| SiPM Detector | MICROFC-30020-SMT-TR1 (3mm x 3mm Silicon Photomultiplier) | [Mouser India](https://www.mouser.in/ProductDetail/onsemi/MICROFC-30020-SMT-TR1?qs=byeeYqUIh0PslEkIwO7UpQ%3D%3D) | 3,400 |
| Charge Amplifier | CR-113-R2-1 Charge Sensitive Preamplifier Module | [Amazon UAE](https://www.amazon.ae/CR-113-R2-1-Charge-Sensitive-preamplifier-Module/dp/B07BCQSBD8) | 12,000 |
| Pulse Shaper | CR-200-500ns-R2-1 Shaping Amplifier (500ns Pulse Time) | [Amazon UAE](https://www.amazon.ae/Cremat-Inc-CR-200-500ns-R2-1-Shaping-Amplifier/dp/B07BD28Y7R) | 12,000 |

**Everhart-Thornley Detector Subtotal: ₹34,100**

---

## Manufacturing Materials

| Component | Description | Link | Cost (INR) |
|-----------|-------------|------|------------|
| 3D Printing Filament | Polypropylene 3D Printer Filament | [Amazon India](https://www.amazon.in/WOL-3D-POLYPROPYLENE-printer-Filament/dp/B08PC3BNV9) | 3,000 |
| Electromagnetic Wire | 20 AWG Enameled Copper "Magnet" Wire (500m) | [Amazon India](https://www.amazon.in/GREENARTZ%C2%AE-Enamelled-Electrical-Winding-Jewellery/dp/B09742PB87/)| 6,250 |
| Soft Iron Core | 99.99% Pure Soft Iron Core, 40mm OD, 100mm Length | [AliExpress](https://ar.aliexpress.com/item/1005009149452245.html) | 3,900 |
| Outer Frame | Al6061-T6 | N/A: Got it in-person | 19,000 |

**Manufacturing Materials Subtotal: ₹13,150**

---

## **TOTAL BOM COST (Parts Ordered): ₹115,969**

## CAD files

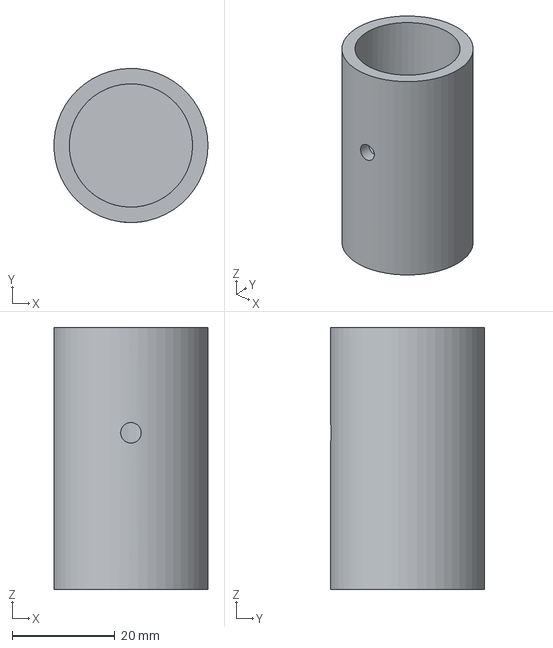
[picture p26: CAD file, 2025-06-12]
assembly/3dprinting/etdetector.step
30.0 x 30.0 x 51.0 mm

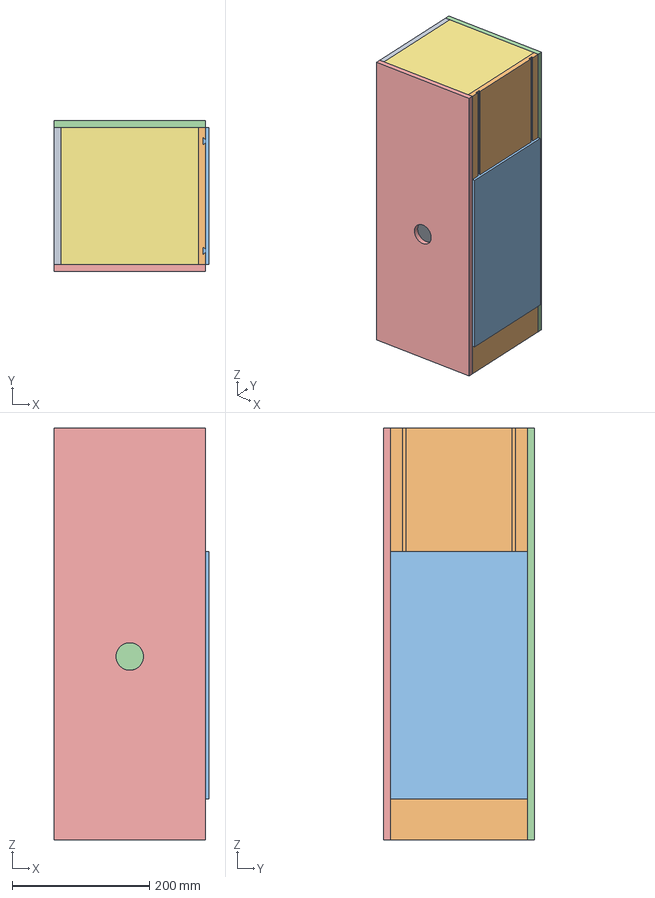
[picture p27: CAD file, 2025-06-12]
assembly/frame.FCStd
225.1 x 220.0 x 600.0 mm
Wall2Al6062
Wall1Al6061
SlidingDoorAl6062
Wall3Alu6061
Wall6Alu6061
Wall5Al6062
Wall4Al6062

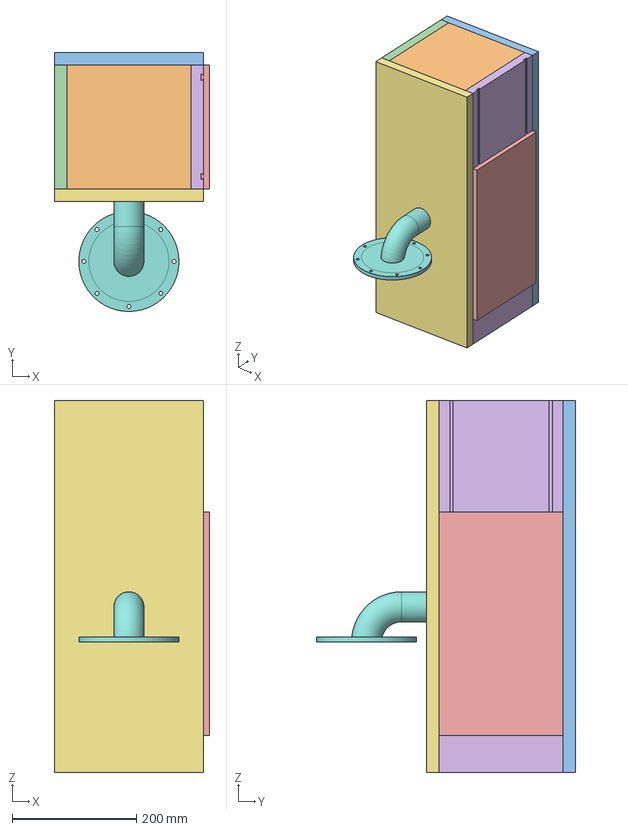
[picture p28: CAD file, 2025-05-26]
cad/Frame.FCStd
250.0 x 417.8 x 600.0 mm
Wall6
Wall4
Wall3
Wall2
SlidingDoor
Wall1
Wall5
VacuumFitting

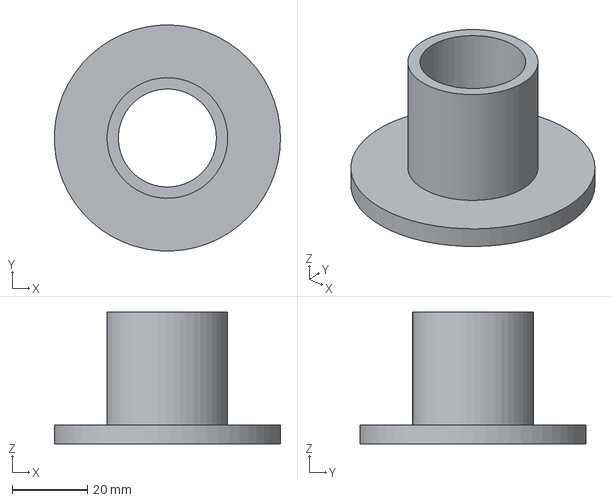
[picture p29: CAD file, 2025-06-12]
assembly/3dprinting/holder.step
60.0 x 60.0 x 35.0 mm

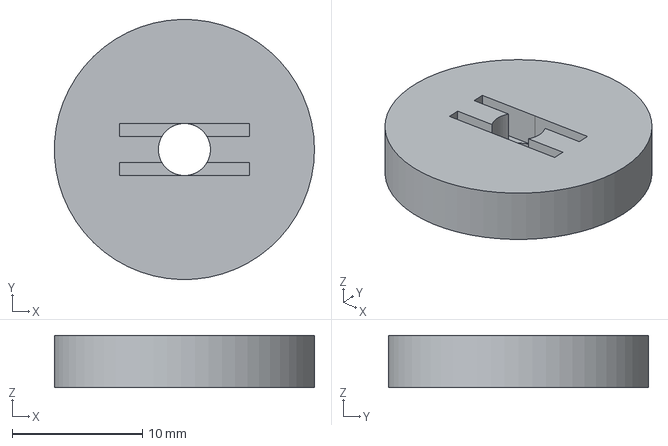
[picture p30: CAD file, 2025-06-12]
assembly/3dprinting/2_times_rasterholder.step
20.0 x 20.0 x 4.00 mm

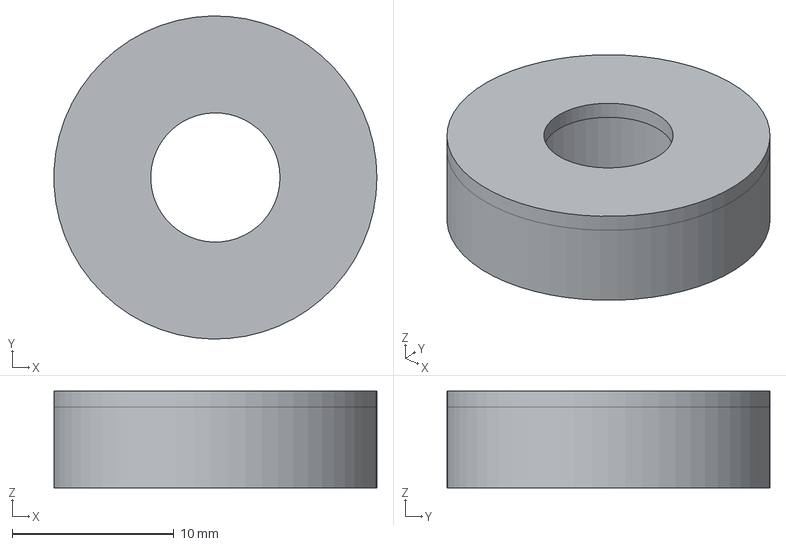
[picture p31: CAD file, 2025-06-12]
assembly/3dprinting/thermholder.step
20.0 x 20.0 x 6.00 mm

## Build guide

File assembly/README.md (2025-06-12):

3D print these files with polypropylene (PP) filament (ABS should work fine but PP is probably better and not inordinately more expensive).

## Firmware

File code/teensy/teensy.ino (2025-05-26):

#include <TMCStepper.h>
#include <SPI.h>

const int STEP1_PIN = 2, DIR1_PIN = 3;
const int STEP2_PIN = 4, DIR2_PIN = 5;
const int STEP3_PIN = 6, DIR3_PIN = 7;
const int EN_PIN = 8;

const int ADC_CS_PIN = 9;
const int ADC_SCLK_PIN = 10;
const int ADC_ECHO_PIN = 11;
const int ADC_SDOA_PIN = 12;
const int ADC_SDOB_PIN = 13;
const int ADC_CNV_PIN = 14;
const int ADC_BUSY_PIN = 15;

const int DAC_CS_PIN = 16;
const int DAC_LDAC_PIN = 17;
const int DAC_CLR_PIN = 18;

const uint8_t DRIVER1_ADDRESS = 0b00;
const uint8_t DRIVER2_ADDRESS = 0b01;
const uint8_t DRIVER3_ADDRESS = 0b10;

const float R_SENSE = 0.11f;
const int MICROSTEPS = 128;
const int STEPS_PER_REV = 200;
const int TOTAL_STEPS_PER_REV = STEPS_PER_REV * MICROSTEPS;

const uint8_t DAC_CMD_WRITE_INPUT_REG = 0x00;
const uint8_t DAC_CMD_UPDATE_DAC_REG = 0x01;
const uint8_t DAC_CMD_WRITE_UPDATE_ALL = 0x02;
const uint8_t DAC_CMD_WRITE_UPDATE_N = 0x03;
const uint8_t DAC_CMD_POWER_DOWN = 0x04;
const uint8_t DAC_CMD_CLEAR_CODE = 0x05;
const uint8_t DAC_CMD_LDAC_REG = 0x06;
const uint8_t DAC_CMD_RESET = 0x07;
const uint8_t DAC_CMD_INTERNAL_REF = 0x08;

TMC2209Stepper driver1(&Serial1, R_SENSE, DRIVER1_ADDRESS);
TMC2209Stepper driver2(&Serial1, R_SENSE, DRIVER2_ADDRESS);
TMC2209Stepper driver3(&Serial1, R_SENSE, DRIVER3_ADDRESS);

struct MotorState {
  long position;
  long targetPosition;
  bool moving;
  unsigned long lastStepTime;
  unsigned long stepInterval;
  int stepPin;
  int dirPin;
};

struct ADCData {
  uint16_t channelA;
  uint16_t channelB;
  bool dataReady;
  unsigned long lastConversion;
};

struct DACData {
  uint16_t channelA;
  uint16_t channelB;
  uint16_t channelC;
  uint16_t channelD;
  bool needsUpdate[4];
};

struct USBCommand {
  char buffer[64];
  int index;
  bool complete;
};

struct StreamData {
  bool enabled;
  unsigned long lastStream;
  unsigned long streamInterval;
};

MotorState motor1 = {0, 0, false, 0, 1000, STEP1_PIN, DIR1_PIN};
MotorState motor2 = {0, 0, false, 0, 1000, STEP2_PIN, DIR2_PIN};
MotorState motor3 = {0, 0, false, 0, 1000, STEP3_PIN, DIR3_PIN};

ADCData adcData = {0, 0, false, 0};
DACData dacData = {0, 0, 0, 0, {false, false, false, false}};
USBCommand usbCmd = {"", 0, false};
StreamData streamData = {false, 0, 1000};

volatile bool echoReceived = false;
volatile int echoBitCount = 0;
volatile uint32_t adcResultA = 0;
volatile uint32_t adcResultB = 0;

void setup() {
  Serial.begin(115200);
  Serial1.begin(115200);
  
  pinMode(STEP1_PIN, OUTPUT); pinMode(DIR1_PIN, OUTPUT);
  pinMode(STEP2_PIN, OUTPUT); pinMode(DIR2_PIN, OUTPUT);
  pinMode(STEP3_PIN, OUTPUT); pinMode(DIR3_PIN, OUTPUT);
  pinMode(EN_PIN, OUTPUT);
  
  pinMode(ADC_CS_PIN, OUTPUT);
  pinMode(ADC_SCLK_PIN, OUTPUT);
  pinMode(ADC_CNV_PIN, OUTPUT);
  pinMode(ADC_ECHO_PIN, INPUT);
  pinMode(ADC_SDOA_PIN, INPUT);
  pinMode(ADC_SDOB_PIN, INPUT);
  pinMode(ADC_BUSY_PIN, INPUT);
  
  pinMode(DAC_CS_PIN, OUTPUT);
  pinMode(DAC_LDAC_PIN, OUTPUT);
  pinMode(DAC_CLR_PIN, OUTPUT);
  
  digitalWrite(EN_PIN, LOW);
  digitalWrite(ADC_CS_PIN, HIGH);
  digitalWrite(ADC_SCLK_PIN, LOW);
  digitalWrite(ADC_CNV_PIN, LOW);
  
  digitalWrite(DAC_CS_PIN, HIGH);
  digitalWrite(DAC_LDAC_PIN, HIGH);
  digitalWrite(DAC_CLR_PIN, HIGH);
  
  SPI.begin();
  SPI.beginTransaction(SPISettings(20000000, MSBFIRST, SPI_MODE1));
  
  attachInterrupt(digitalPinToInterrupt(ADC_ECHO_PIN), echoISR, RISING);
  
  initializeDriver(driver1);
  initializeDriver(driver2);
  initializeDriver(driver3);
  
  initializeADC();
  initializeDAC();
}

void initializeDriver(TMC2209Stepper &driver) {
  driver.begin();
  driver.toff(5);
  driver.rms_current(800);
  driver.microsteps(MICROSTEPS);
  driver.pwm_autoscale(true);
  driver.en_spreadCycle(false);
  driver.interpolation(true);
}

void initializeADC() {
  digitalWrite(ADC_CS_PIN, LOW);
  delayMicroseconds(1);
  digitalWrite(ADC_CS_PIN, HIGH);
  delayMicroseconds(10);
}

void initializeDAC() {
  dacWriteCommand(DAC_CMD_RESET, 0, 0);
  delay(1);
  dacWriteCommand(DAC_CMD_INTERNAL_REF, 0, 0x0001);
  dacWriteCommand(DAC_CMD_POWER_DOWN, 0, 0x0000);
  dacWriteCommand(DAC_CMD_CLEAR_CODE, 0, 0x8000);
  dacWriteAll(0x8000);
}

void loop() {
  updateMotors();
  updateADC();
  updateDAC();
  processUSBCommands();
  streamADCData();
}

void updateMotors() {
  updateMotor(motor1);
  updateMotor(motor2);
  updateMotor(motor3);
}

void updateMotor(MotorState &motor) {
  if (!motor.moving) return;
  
  if (micros() - motor.lastStepTime >= motor.stepInterval) {
    digitalWrite(motor.stepPin, HIGH);
    delayMicroseconds(2);
    digitalWrite(motor.stepPin, LOW);
    
    if (motor.targetPosition > motor.position) {
      motor.position++;
    } else {
      motor.position--;
    }
    
    if (motor.position == motor.targetPosition) {
      motor.moving = false;
    }
    
    motor.lastStepTime = micros();
  }
}

void updateADC() {
  if (micros() - adcData.lastConversion >= 0.1) {
    startADCConversion();
    adcData.lastConversion = micros();
  }
  
  if (echoReceived && echoBitCount >= 16) {
    adcData.channelA = (adcResultA >> 2) & 0x3FFF;
    adcData.channelB = (adcResultB >> 2) & 0x3FFF;
    adcData.dataReady = true;
    echoReceived = false;
    echoBitCount = 0;
    adcResultA = 0;
    adcResultB = 0;
  }
}

void updateDAC() {
  for (int i = 0; i < 4; i++) {
    if (dacData.needsUpdate[i]) {
      uint16_t value;
      switch (i) {
        case 0: value = dacData.channelA; break;
        case 1: value = dacData.channelB; break;
        case 2: value = dacData.channelC; break;
        case 3: value = dacData.channelD; break;
      }
      dacWriteChannel(i, value);
      dacData.needsUpdate[i] = false;
    }
  }
}

void startADCConversion() {
  digitalWrite(ADC_CNV_PIN, HIGH);
  delayMicroseconds(1);
  digitalWrite(ADC_CNV_PIN, LOW);
  
  digitalWrite(ADC_CS_PIN, LOW);
  echoBitCount = 0;
  adcResultA = 0;
  adcResultB = 0;
}

void echoISR() {
  if (echoBitCount < 16) {
    adcResultA = (adcResultA << 1) | digitalReadFast(ADC_SDOA_PIN);
    adcResultB = (adcResultB << 1) | digitalReadFast(ADC_SDOB_PIN);
    echoBitCount++;
    
    if (echoBitCount >= 16) {
      digitalWrite(ADC_CS_PIN, HIGH);
      echoReceived = true;
    }
  }
}

void moveMotor(int motorNum, long steps) {
  MotorState* motor = getMotor(motorNum);
  if (!motor) return;
  
  motor->targetPosition = motor->position + steps;
  digitalWrite(motor->dirPin, steps > 0 ? HIGH : LOW);
  delayMicroseconds(10);
  motor->moving = true;
}

void moveMotorTo(int motorNum, long position) {
  MotorState* motor = getMotor(motorNum);
  if (!motor) return;
  
  long steps = position - motor->position;
  moveMotor(motorNum, steps);
}

void setMotorSpeed(int motorNum, float rpm) {
  MotorState* motor = getMotor(motorNum);
  if (!motor) return;
  
  motor->stepInterval = (60L * 1000000L) / (rpm * TOTAL_STEPS_PER_REV);
}

void stopMotor(int motorNum) {
  MotorState* motor = getMotor(motorNum);
  if (!motor) return;
  
  motor->moving = false;
  motor->targetPosition = motor->position;
}

void stopAllMotors() {
  stopMotor(1);
  stopMotor(2);
  stopMotor(3);
}

void homeMotor(int motorNum) {
  MotorState* motor = getMotor(motorNum);
  if (!motor) return;
  
  motor->position = 0;
  motor->targetPosition = 0;
  motor->moving = false;
}

void homeAllMotors() {
  homeMotor(1);
  homeMotor(2);
  homeMotor(3);
}

bool isMotorMoving(int motorNum) {
  MotorState* motor = getMotor(motorNum);
  return motor ? motor->moving : false;
}

bool anyMotorMoving() {
  return motor1.moving || motor2.moving || motor3.moving;
}

long getMotorPosition(int motorNum) {
  MotorState* motor = getMotor(motorNum);
  return motor ? motor->position : 0;
}

MotorState* getMotor(int motorNum) {
  switch(motorNum) {
    case 1: return &motor1;
    case 2: return &motor2;
    case 3: return &motor3;
    default: return nullptr;
  }
}

void setMotorCurrent(int motorNum, uint16_t current) {
  switch(motorNum) {
    case 1: driver1.rms_current(current); break;
    case 2: driver2.rms_current(current); break;
    case 3: driver3.rms_current(current); break;
  }
}

void enableMotors() {
  digitalWrite(EN_PIN, LOW);
}

void disableMotors() {
  digitalWrite(EN_PIN, HIGH);
}

uint16_t getADCChannelA() {
  if (adcData.dataReady) {
    adcData.dataReady = false;
    return adcData.channelA;
  }
  return 0;
}

uint16_t getADCChannelB() {
  if (adcData.dataReady) {
    return adcData.channelB;
  }
  return 0;
}

bool isADCDataReady() {
  return adcData.dataReady;
}

float adcToVoltage(uint16_t adcValue) {
  return (adcValue * 5.0) / 16383.0;
}

void dacWriteCommand(uint8_t cmd, uint8_t address, uint16_t data) {
  uint32_t packet = ((uint32_t)cmd << 19) | ((uint32_t)address << 16) | data;
  
  digitalWrite(DAC_CS_PIN, LOW);
  SPI.transfer((packet >> 16) & 0xFF);
  SPI.transfer((packet >> 8) & 0xFF);
  SPI.transfer(packet & 0xFF);
  digitalWrite(DAC_CS_PIN, HIGH);
}

void dacWriteChannel(uint8_t channel, uint16_t value) {
  dacWriteCommand(DAC_CMD_WRITE_UPDATE_N, channel, value);
}

void dacWriteAll(uint16_t value) {
  dacWriteCommand(DAC_CMD_WRITE_UPDATE_ALL, 0, value);
}

void setDACChannel(uint8_t channel, uint16_t value) {
  if (channel > 3) return;
  
  switch (channel) {
    case 0: dacData.channelA = value; break;
    case 1: dacData.channelB = value; break;
    case 2: dacData.channelC = value; break;
    case 3: dacData.channelD = value; break;
  }
  dacData.needsUpdate[channel] = true;
}

void setDACVoltage(uint8_t channel, float voltage) {
  if (voltage < -10.0) voltage = -10.0;
  if (voltage > 10.0) voltage = 10.0;
  
  uint16_t dacValue = (uint16_t)((voltage + 10.0) * 65535.0 / 20.0);
  setDACChannel(channel, dacValue);
}

uint16_t getDACChannel(uint8_t channel) {
  switch (channel) {
    case 0: return dacData.channelA;
    case 1: return dacData.channelB;
    case 2: return dacData.channelC;
    case 3: return dacData.channelD;
    default: return 0;
  }
}

float dacToVoltage(uint16_t dacValue) {
  return (dacValue * 20.0 / 65535.0) - 10.0;
}

void processUSBCommands() {
  while (Serial.available()) {
    char c = Serial.read();
    
    if (c == '\n' || c == '\r') {
      if (usbCmd.index > 0) {
        usbCmd.buffer[usbCmd.index] = '\0';
        parseCommand(usbCmd.buffer);
        usbCmd.index = 0;
      }
    } else if (usbCmd.index < 63) {
      usbCmd.buffer[usbCmd.index++] = c;
    }
  }
}
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

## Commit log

2025-05-08 Update Bill of Materials.docx
2025-05-11 added wehnelt_cap
    [WehneltCap.FCStd, WehneltCap.step]
2025-05-11 einzel lenses
    [CondenserLens.FCStd, CondenserLens.step, ObjectiveLens.FCStd, ObjectiveLens.step]
2025-05-17 MAGNETIC LENSES???? YEAH!
2025-05-19 electron gun, success!
    [save.step, wehnelt.step]
2025-05-20 empirical utilization
    using values from a paper for fabbing the SEM. HUGE improvement
    [Anode.FCStd, Condenser.FCStd, Objective.FCStd, WehneltCylinder.FCStd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]
2025-05-20 better org by function rather than semantics
    [Anode.FCStd, Condenser.FCStd, ElectronColumn.FCStd, Objective.FCStd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]
2025-05-21 diffusion pump info
2025-05-21 cad accuracy update
    [ElectronColumn.FCStd, SiPM.stp]
2025-05-23 updates to readme
    [ElectronColumn.FCStd, SiPM.stp]
2025-05-24 electron column structural components
    [ElectronColumn.FCStd]
2025-05-24 name change
    [Column.FCStd]
2025-05-26 completed frame
    [Frame.FCStd]
2025-05-26 frame changes
    [Frame.FCStd]
2025-05-26 stepper motor code
2025-05-31 teensy 4.1
2025-06-01 frame and column only
2025-07-05 fixed diffusion pump flanges. ordered water cooling.
